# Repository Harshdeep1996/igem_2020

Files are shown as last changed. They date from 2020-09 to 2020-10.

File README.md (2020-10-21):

# iGEM 2020 - EPFL team's Github
This repository has the necessary code, CAD and circuit files in order to build your own ExpressEAU.

### Project Abstract

Water is an essential resource that we regularly use for drinking, cooking and food processing. Hence, it is important to ensure that it is safe for consumption. EspressEAU serves as an analysis of general water quality. We aimed to create a safe, low-cost, and easy-to-use system that can enable on-site testing of water at home or in small communities. We hypothesized that genetically engineered yeast could be used as biosentinels by hijacking the yeast stress response pathway using either deletion strains or fluorescent reporter strains that are sensitive to water contaminants. These biosentinels are grown in a DIY system with temperature control, stirring, and two optical detectors for fluorescence and density, allowing us to monitor growth and fluorescence of the yeast, and thus detect the presence of contaminants in the water sample. We hope our project will facilitate frequent water testing of local water sources.

### Software used

1. Tinkercad: Used to make the CAD designs for 3D print, using `STL` files (https://www.tinkercad.com/)
2. Circuit Diagram: Used to make circuit schematics using an online IDE (https://www.circuit-diagram.org/)
3. PRUSA 3D Slicer: Used to generate the G Code and the sliced version of the 3D element (https://www.prusa3d.com/drivers/)
4. Processing: Used to interface between the Arduino Serial Interface and to collect data on the host machine (https://processing.org/)

### Hardware Components used

#### Microcontroller: Arduino Uno
Arduino_Uno

[Source](https://www.arduino.cc/en/Guide/ArduinoUno)

### Cable: USB for data transfer
USB cable

[Datasheet](https://www.arduino.cc/documents/datasheets/USBcable.PDF)\
[Source](https://store.arduino.cc/usb-2-0-cable-type-a-b?queryID=aa479172c324b5d009057f23eaddd86c)

#### Temperature Sensor: TMP36
TMP36

[Datasheet](https://www.analog.com/en/products/tmp36.html)\
[Source](https://learn.adafruit.com/tmp36-temperature-sensor)

#### Light to Frequency Sensor: TSL235R (primarily for optical density measurement)
light_to_frequency

[Datasheet](https://www.sparkfun.com/datasheets/Sensors/Imaging/TSL235R-LF.pdf)\
[Source](https://www.sparkfun.com/products/9768)

#### RGB Light Sensor: ISL9125 (primarily for fluorescence measurement)
TMP36

[Datasheet](https://cdn.sparkfun.com/datasheets/Sensors/LightImaging/isl29125.pdf)\
[Source](https://www.sparkfun.com/products/12829)

#### OEM Temperature sensor: DS18B20 (for calibration and check of TMP36 sensor)
DS18B20

[Datasheet](https://datasheets.maximintegrated.com/en/ds/DS18B20.pdf)\
[Source](https://www.digitec.ch/de/s1/product/oem-ds18b20-sensor-elektronikmodul-8030174)

#### Power Supply 9V, 1.5A (Variable): 3 V - 12 V universal power supply 1.5A
TMP36

[Source](https://www.distrelec.ch/en/power-supply-9v-600ma-4w-nordic-power-am-04159a-9v/p/16968715?channel=b2c&price_gs=10.41459&source=googleps&ext_cid=shgooaqchen-na&utm_source=google&utm_medium=surfaces&utm_campaign=surfaces_across_google_chen&ext_cid=shgooaqchen-p-shopping-fallback&gclid=EAIaIQobChMI96_OxLfE7AIVg-3tCh1RsQ7TEAQYASABEgLpjPD_BwE)

#### Thermoelectric Peltier Element: TEC1-12706
TEC1-12706

[Datasheet](https://peltiermodules.com/peltier.datasheet/TEC1-12706.pdf)\
[Source](https://protosupplies.com/product/tec1-12706-thermoelectric-peltier-cooling-device/)

#### IRF520 Mosfet Transistor
ESC

[Datasheet](https://www.vishay.com/docs/91017/91017.pdf)\
[Source](https://www.aliexpress.com/)

#### DC Motor (working with 6V or 9V - 9V is generally more consistent)

DCMotor_

[Datasheet](https://www.arduino.cc/documents/datasheets/DCmotor.PDF)\
[Source](https://aliexpress.com)

#### Pack of LEDs - white LED and Orange LED (with wave length between 530-560 nm for fluorescence measurement) 
#### Battery 9V
#### Jumper wires (types: Male-Female, Female-Female, Male-Male)
#### Soldering iron with tin
#### Glue gun (with glue sticks)

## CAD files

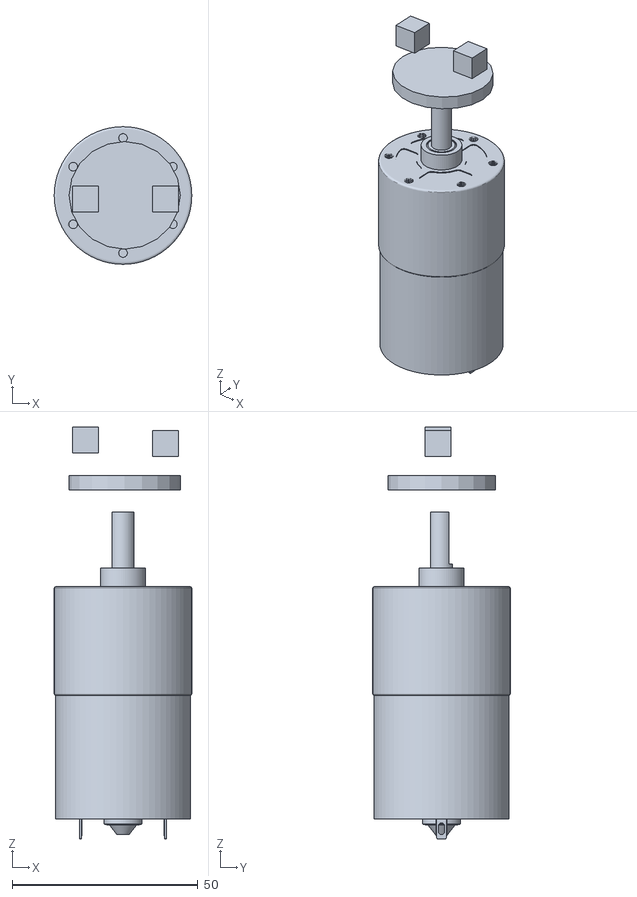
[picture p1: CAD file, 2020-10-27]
exploded_view_magnetic_stirrer.stl
37.1 x 37.1 x 111.0

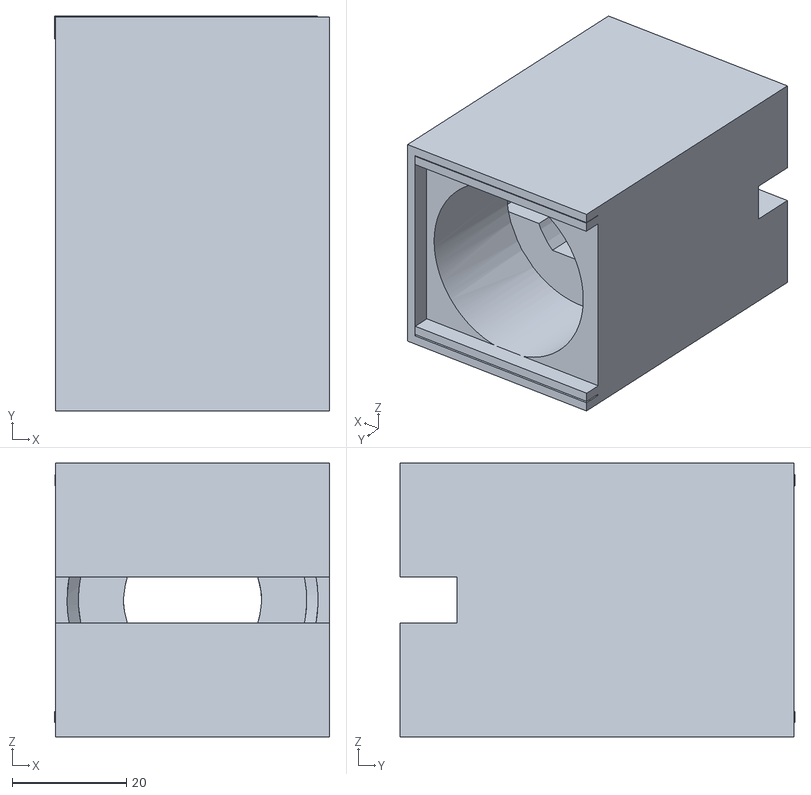
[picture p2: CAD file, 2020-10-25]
base_component_holding_motor_final.STL
48.2 x 69.2 x 48.0

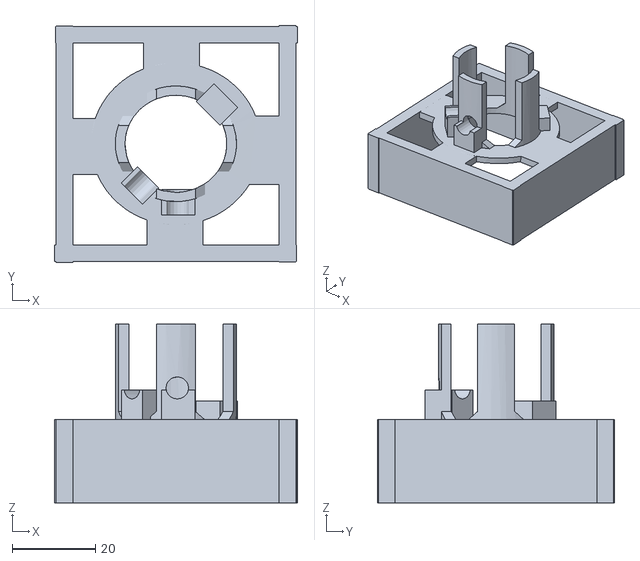
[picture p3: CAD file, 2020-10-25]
top_component_holding_vial_v5_final.STL
58.5 x 57.0 x 43.0

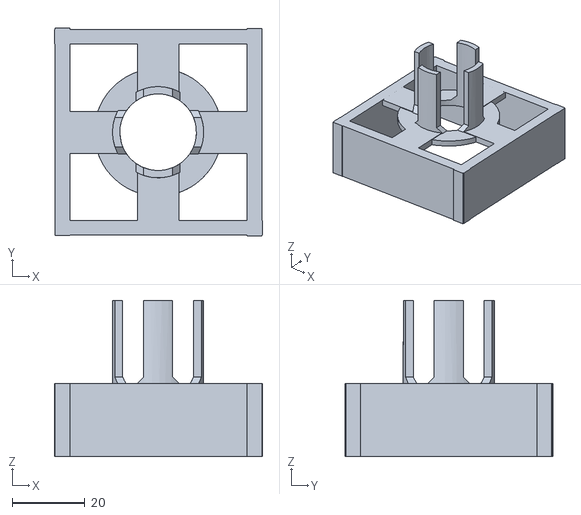
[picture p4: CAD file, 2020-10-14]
top_component_holding_vial_v4.STL
57.0 x 57.1 x 42.8

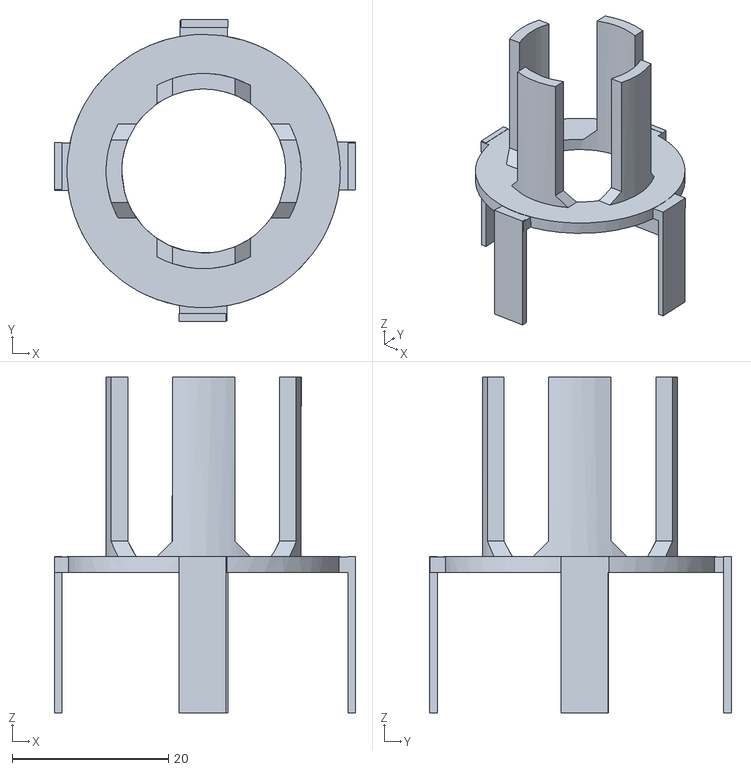
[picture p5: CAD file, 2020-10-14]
top_component_holding_vial_v2.STL
38.6 x 38.6 x 43.0

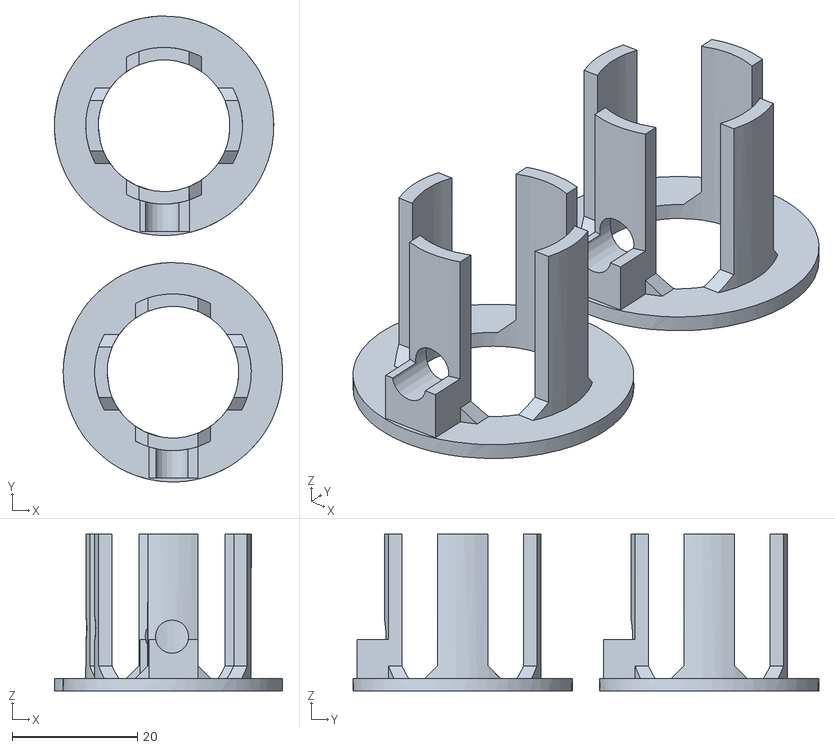
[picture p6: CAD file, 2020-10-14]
top_component_holding_vial_v3.STL
36.4 x 74.3 x 25.0

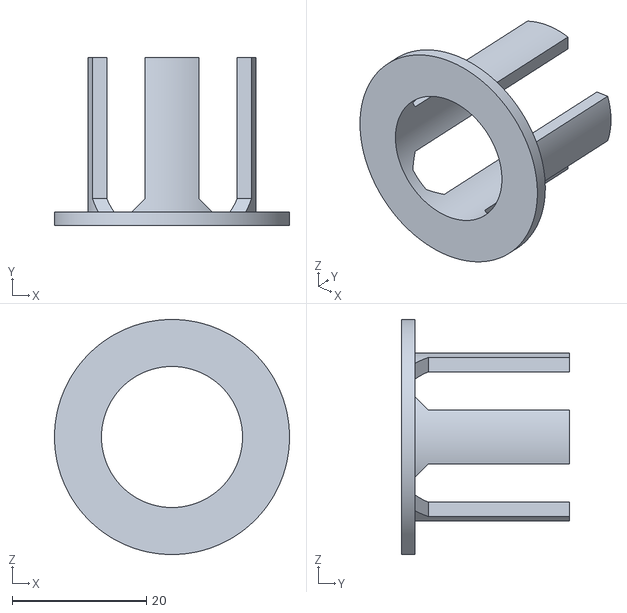
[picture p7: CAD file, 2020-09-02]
top_component_holding_vial_v1.STL
35.0 x 25.0 x 35.0

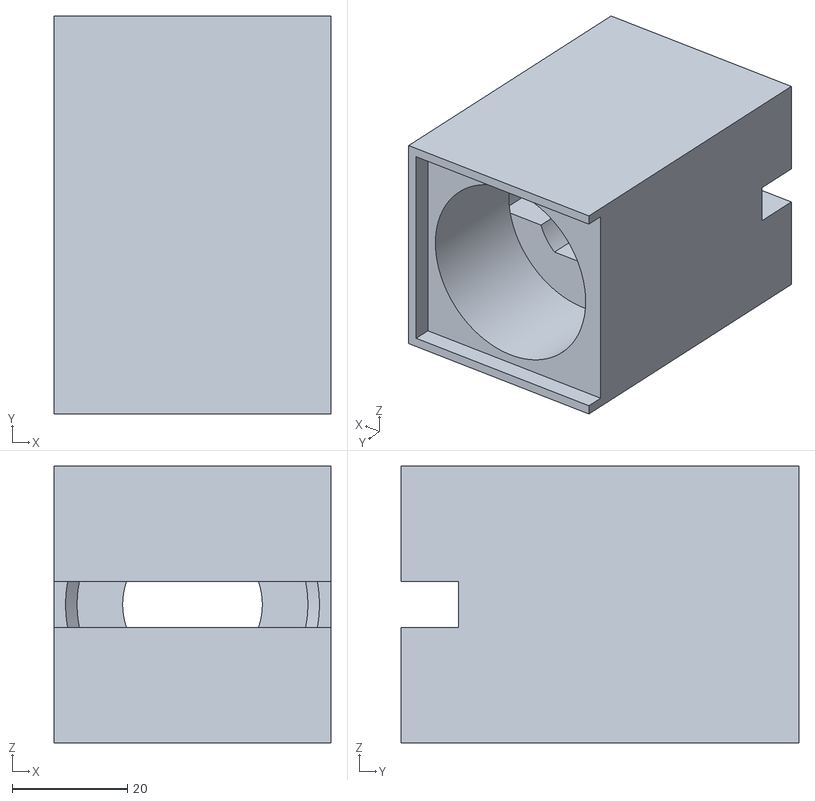
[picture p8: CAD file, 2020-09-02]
base_motor_peltier_v1.STL
48.0 x 69.0 x 48.0

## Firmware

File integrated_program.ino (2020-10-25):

#include <Wire.h>
#include "SFE_ISL29125.h"
#include <SPI.h>
#include <SD.h>

bool OD_MESUREMENT = false;
bool verbose = true;


/*
 * Relative to the TSL235r
 */
int tsl_input_pin = 2;
volatile unsigned long cnt = 0;
unsigned long oldcnt = 0;
unsigned long t = 0;
unsigned long last;
void irq1()
{
  cnt++;
}

// Welcome attentive viewer, who paused the video to see what the code looks like! 
//Great job...

/* 
 *  Relative to the white LED
 */
int white_light_pin = 3;
/*
 * Relative to the RGB light sensor
 */
 SFE_ISL29125 RGB_sensor;

int red_low = 480;
int red_high = 3860;
int green_low = 770;
int green_high = 5950;
int blue_low = 575;
int blue_high = 4400;

/*
 * Relative to the yellow LED
 */
int yellow_light_pin = 4;
 
/*
 * Main
 */

int switch_cnt = 0;
int THRESHOLD = 1;


// for the temperature sensor
unsigned long previousMillis = 0;
const int outputPin_tmp = 5;
const int temperaturePin = A0;

void switch_mode(){
  switch_cnt = 0;
  OD_MESUREMENT = !OD_MESUREMENT;

  //if (verbose){
    Serial.println("SWITCH!");
  //}
  if (OD_MESUREMENT){
  //  if(verbose){
  //    Serial.println("Start OD mesurement");
  //  }
    tsl_input_pin = 2;
    cnt = 0;
    oldcnt = 0;
    t = 0;
    last = millis();
    digitalWrite(yellow_light_pin, LOW);
    digitalWrite(white_light_pin, HIGH);
  } else {
    //if(verbose){
    //  Serial.print("Start fluorescence mesurement ");
    //  Serial.println("(using yellow led approx 580 nm)");
    //}
    digitalWrite(yellow_light_pin, HIGH);
    digitalWrite(white_light_pin, LOW);
  }
}

void setup() {
  Serial.begin(9600);

  //TSL235r setup
  Serial.println("START");
  pinMode(tsl_input_pin, INPUT);
  digitalWrite(tsl_input_pin, HIGH);
  attachInterrupt(0, irq1, RISING);

  //Yellow LED setup
  pinMode(yellow_light_pin, OUTPUT);

  //White LED setup
  pinMode(white_light_pin, OUTPUT);

  pinMode(outputPin_tmp, OUTPUT);
  
  //RGB light sensor setup
  if (RGB_sensor.init()){
    Serial.println("Sensor Initialization Successful\n\r");
  }
  switch_mode();
}

void od_mesurements(){
    if (millis() - last >= 1000){      
      switch_cnt += 1;
      last = millis();
      t = cnt;
      unsigned long hz = t - oldcnt;
      
      Serial.print(millis()); 
      Serial.print(" FREQ: "); 
      Serial.print(hz);
      Serial.print("\t = "); 
      Serial.print((hz+50)/100);  // +50 == rounding last digit
      Serial.println(" mW/m2");
      oldcnt = t;
    }
}

void fluo_mesurements(){      
  switch_cnt += 1;

  unsigned int red = RGB_sensor.readRed();
  unsigned int green = RGB_sensor.readGreen();
  unsigned int blue = RGB_sensor.readBlue();

  int redV = map(red, red_low, red_high, 0, 255);
  int redVal = constrain(redV, 0, 255);

  int greenV = map(green, green_low, green_high, 0, 255);
  int greenVal = constrain(greenV, 0, 255);

  int blueV = map(blue, blue_low, blue_high, 0, 255);
  int blueVal = constrain(blueV, 0, 255);
  Serial.print(millis());
  Serial.print(" Red: "); Serial.print(redVal);
  Serial.print(", ");
  Serial.print("Green: "); Serial.print(greenVal);
  Serial.print(", ");
  Serial.print("Blue: "); Serial.print(blueVal);
  Serial.println();
}

float getVoltage(int pin)
{
  return (analogRead(pin) * 0.004882814);
}

const int total_interval = 25000;

void loop() {

  float voltage, degreesC;
  boolean switcher;
  
  voltage = getVoltage(temperaturePin);
  degreesC = (voltage - 0.5) * 100.0;
  Serial.print(millis());
  Serial.print("  deg C: ");
  Serial.println(degreesC);

  // unsigned long currentMillis = millis();


  if(previousMillis >= total_interval) {
    previousMillis = 0;
  }

  if (degreesC > 31){
    digitalWrite(outputPin_tmp, LOW);
    delay(8000);
    previousMillis += 8000;
  }
  if (degreesC < 29){
    if (degreesC < 20) {
      digitalWrite(outputPin_tmp, LOW);
      delay(8000);
      previousMillis += 8000;
   } else {
       digitalWrite(outputPin_tmp, HIGH);
       delay(3000);
       previousMillis += 3000;
   }
  }

  if((previousMillis + 3000 >= total_interval) && (previousMillis + 8000 >= total_interval) && (previousMillis > total_interval)) {
    if(switch_cnt == THRESHOLD){
      switch_mode();
    }
    // put your main code here, to run repeatedly:
    if (OD_MESUREMENT){
     od_mesurements();
    } else {
      fluo_mesurements();
    }
  }
}

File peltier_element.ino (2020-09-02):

const int outputPin = 3;
const int temperaturePin = A0;


void setup() {
  Serial.begin(9600);
  pinMode(outputPin, OUTPUT);
  
  
}

void loop() {
  float voltage, degreesC;
  boolean switcher;
  
  voltage = getVoltage(temperaturePin);
  degreesC = (voltage - 0.5) * 100.0;
  Serial.print("  deg C: ");
  Serial.println(degreesC);

  if (degreesC > 31){
    digitalWrite(outputPin, LOW);
  }
  if (degreesC < 29){
    digitalWrite(outputPin, HIGH);
  }
  
  delay(100);

}

float getVoltage(int pin)
{
  return (analogRead(pin) * 0.004882814);
}

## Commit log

2020-09-02 adding the lower part of the housing for the magnet
    [part_one_housing.STL]
2020-09-02 adding the upper part of the housing holding the tube
    [part_two_housing.STL]
2020-09-02 code for peltier element and temperature check
2020-09-03 adding circuit iteration with temperature sensor, peltier and dc
2020-10-14 Adding file for OD sensor and fluroscence
2020-10-14 adding circuit for magnetic stirrer
2020-10-14 renaming STL files
    [base_motor_peltier_v1.STL, top_component_holding_vial_v1.STL]
2020-10-14 adding v5 for the top component holding vial
    [top_component_holding_vial_v5.STL]
2020-10-14 adding top vial component v2
    [top_component_holding_vial_v2.STL]
2020-10-14 adding top component with v4
    [top_component_holding_vial_v4.STL]
2020-10-20 adding print writer for arduino
2020-10-21 changing picture for DC motor
2020-10-21 adding the arduino uno picture, and fixing MD problems
2020-10-21 changing names of the sensor, next lines
2020-10-22 adding print writer
2020-10-25 adding gitignore and renaming the file to v3 and v5
    [top_component_holding_vial_v3.STL]
2020-10-25 adding vial component holder
    [top_component_holding_vial_v5_final.STL]
2020-10-25 adding the base component STL file
    [base_component_holding_motor_final.STL]
2020-10-27 exploded view the stirrer
    [exploded_view_magnetic_stirrer.stl]
